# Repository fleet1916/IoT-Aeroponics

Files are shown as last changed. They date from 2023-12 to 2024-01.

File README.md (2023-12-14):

# IoT-Aeroponics
Authors: Zheyuan Zheng (zz534@cornell.edu), Kyle Harris (kah289@cornell.edu), Department of Mechanical and Aerospace Engineering, Cornell University. 
Under the support of Prof. Perrine Pepiot, MAE and Prof. Magdalena Maria Julkowska, Boyce Thompson Institute. 

An basic IoT solution for aeroponics system control based on Arduino 
This project uses a ESP 8266 to set up WiFi and server to allow the control of multiple aeroponics systems to raise multiple plants. 
It includes 4 basic types of the station: The Main Control Terminal (MCT), The Bucket Control Station (BCS), Data Collection and Calibration Station (DCS), and In Bucket Stand (IBS). 
A set of system would include 1 MCT, maximum of ( 8 BCS + 40 IBS ) and 1 DCS. 
The Main Control Terminal sends out input command through a WiFi server. All the bucket control station connects and receives the signal from the server to determine the bucket number, mode and control perimeter.

The Bucket Control Station controls 5 bucket. It can operate the 5 buckets'mist makers separately in time control mode, percentage control mode and on/off mode. It also provide power for the fans that distribute the mist evenly in the buckets as well.                     
Time control mode turns on the mistmaker for X seconds and turn off the mistmaker for Y seconds. X and Y can be input through the MCT. 
Percentage mode set the mist level to a certain IR sensor reading by turning on and off the mist maker . 
This reading is determined by a steady state mist level IR sensor reading multiplied by the percentage input throught he MCT. 
For the on/off mode, the MCT can control the mist maker on/off directly 

The Data Collection and Calibration Station have no control authority over mist maker and the fan. It is a interface to record the mist level in the bucket during normal operation and determine the steady state IR sensor reading for calibration purposes, which is necessary for the Percentage mode to work properly. Sensor value A is obtained by reading the sensor value without turning on the mist maker.  Another sensor value B can be obtained by set the bucket control mode to on/off and turn on the mist maker for more than 20 mins. The calibration reading is the absolute value of the difference between A and B. After getting the calibration reading, change the fullmist value to the calibration value for the control mode to operate in its best condition. 

The In Bucket Stand is a stand to host fan and sensor for the controlling and mist distribution purposes. It needs to be connected to the BCS. 

Look for the bill of materials and assembly insturction to make the system and installing libraries in you computer. 
Upload the code in each folder to the corresponding arduino/ESP8266 board to set up the functions of the system

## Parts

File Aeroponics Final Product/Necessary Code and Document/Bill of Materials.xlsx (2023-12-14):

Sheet: Main Control Terminal
Name | Quantity | Amazon ASIN | Amazon name | Note
Arduino MEGA 2560 controller | 1 | N/A
PCB | 1 | B0BK76L5BD | SchmalzTech Double Sided ENIG Protoboard, Solderable Breadboard, Electronic Circuit Board for DIY Prototype Circuit, FR4, Plated Through Hole Solder Prototype Board, ST-Proto (1" x 2")
Dupont wires | 17 |  |  | Assorted dupont female- male, male-male jumper wires
Female Dupont Connector | 6
Short jumper wires | 4
ESP8266 WiFi Module | 1 | B010N1ROQS | HiLetgo 3pcs ESP8266 ESP-01 Serial WiFi Wireless Transceiver Wireless Module Development Board LWIP AP+STA Compatible with Arduino
Keypad | 1 | B086ZGKDK9 | DIYmalls 4x4 Matrix Membrane Keypad 16 Key Keyboard Module Array Switch for Arduino ESP32
LCD screen | 1 | B0C6SGK21R | DIYmalls 20x4 IIC I2C 2004 LCD Display Screen Module 5V White Character Blue Backlight with Serial Adapter Board PCF8574 for Arduino (Pack of 2)
Header Pin | 14
Remote Control Casing | 1 |  |  | CAD in Github

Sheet: Bucket Control Station
Name | Quantity | Amazon ASIN | Amazon name | Note
Arduino Nano | 1 | ‎B0713XK923 | ELEGOO Nano Board CH 340/ATmega+328P Without USB Cable, Compatible with Arduino Nano V3.0 (Nano x 3 Without Cable)
PCB | 2 | B0BK76L5BD | SchmalzTech Double Sided ENIG Protoboard, Solderable Breadboard, Electronic Circuit Board for DIY Prototype Circuit, FR4, Plated Through Hole Solder Prototype Board, ST-Proto (1" x 2")
Relay | 5 | B07BVXT1ZK | ARCELI 5PCS 5V One Channel Relay Module Board Shield 5v Relay Module for PIC AVR DSP ARM for Relay | Note that in Amazon introduction, it sasy the coil voltage is 12V. But the actual coil voltage is 5 V, which is correct for our application
WiFi Module | 1 | B010N1ROQS | HiLetgo 3pcs ESP8266 ESP-01 Serial WiFi Wireless Transceiver Wireless Module Development Board LWIP AP+STA Compatible with Arduino
Switch | 6 | B07XC5KB8D | TWTADE 10Pcs Rocker Switch ON/Off SPST 2Pin Latching Toggle Switch Snap Round with Pre-Wired 6A/250V 10A/125V AC for Boat,Car etc.KCD1-X-Y
Power Distribution Panel | 1 | B093PWRJS9 | WayinTop PCB Double-Layer Wiring Power Distribution Board Kit, 2 x 12 Position Power Distribution Module 2 Inputs 2 x 13 Outputs for DC AC 24V 10A
Voltage Converter | 1 | B076P4C42B | Wolfwhoop PW-D Control Buck Converter 6-24V to 5V 1.5A Step-Down Regulator Module Power Inverter Volt Stabilizer
LED | 6 | N/A |  | Any 5V LED would work
heat shrink tube | 1 | N/A
Female Dupont Connector | 6 | N/A
Female Round 2.1mm*5.5 mm | 6 | B071VTBQNG | MILAPEAK (Real 18AWG 43x2pcs Wires) 20pcs Female DC Power Pigtail Cable, 12V 5A DC Connectors for CCTV Security Camera and Lighting Power Adapter (2.1mm x 5.5mm, Ultra Thick)
Jumper Wires |  | N/A
JST-XH connector | 10 | B07YKHV46N | 5 Pairs JST-XH 2.54mm 1S 2 Pin Balance Plug Lead Socket Male and Female Connector with 10cm Silicone Wire Cables for Woodland Just Plug Lights 3D Printer
Power Source |  | B08Z7X9F1V | 24 Volt 6 Amp Power Supply Adapter,100-240V AC to DC 24V 6A Power Adapter with 5.5mm x 2.1mm DC Output Jack Transformers US Plug for LED Strip Light,Security Cameras,Printer
Switch Box | 1 |  |  | CAD in Github

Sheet: Data Collection and Calibration
Name | Quantity | Amazon ASIN | Amazon name | Note
PCB | 1 | B0BK76L5BD | SchmalzTech Double Sided ENIG Protoboard, Solderable Breadboard, Electronic Circuit Board for DIY Prototype Circuit, FR4, Plated Through Hole Solder Prototype Board, ST-Proto (1" x 2")
Arduino Nano | 1 | ‎B0713XK923 | ELEGOO Nano Board CH 340/ATmega+328P Without USB Cable, Compatible with Arduino Nano V3.0 (Nano x 3 Without Cable)
LCD | 1 | B071Y6JX3H | SunFounder LCD1602 Module with 3.3V Backlight Compatible with Arduino R3 Mega2560 Raspberry Pi 16x2 Character White on Blue Background
Jumper Wire
Potentiometer for Arduino | 1
JST-XH connector | 10 | B07YKHV46N | 5 Pairs JST-XH 2.54mm 1S 2 Pin Balance Plug Lead Socket Male and Female Connector with 10cm Silicone Wire Cables for Woodland Just Plug Lights 3D Printer

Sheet: In Barrel Stand
Name | Quantity (per Bucket) | Amazon ASIN | Amazon name | Note
24V Fan | 1 | B00N1Y3T9G | GDSTIME 80mm x 80mm x 25mm 24V Brushless DC Cooling Fan
Infrared Sensor | 1
Mist Maker | 1 | B00P91ZFPA | AGPTEK Aluminum Mini Mist Maker Fogger Water Fountain Pond Fog Machine Atomizer, Perfect for Halloween, Christmas and Other Holidays
Fan and Sensor stand | 1 |  |  | CAD in Github

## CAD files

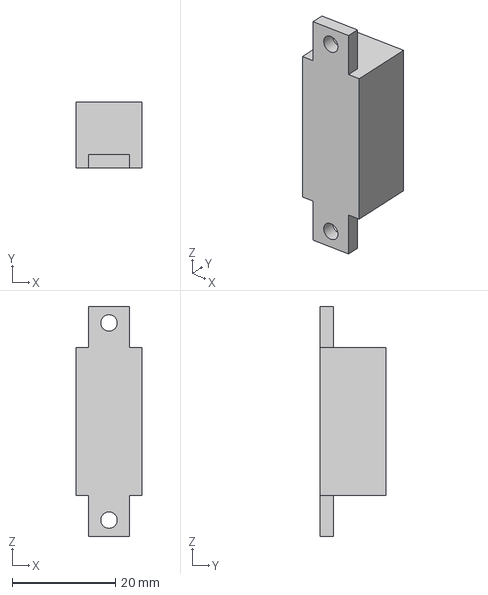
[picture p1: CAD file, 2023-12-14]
Aeroponics Final Product/CAD Files/Electronic Models/Infrared Sensor.step
12.7 x 12.7 x 44.4 mm

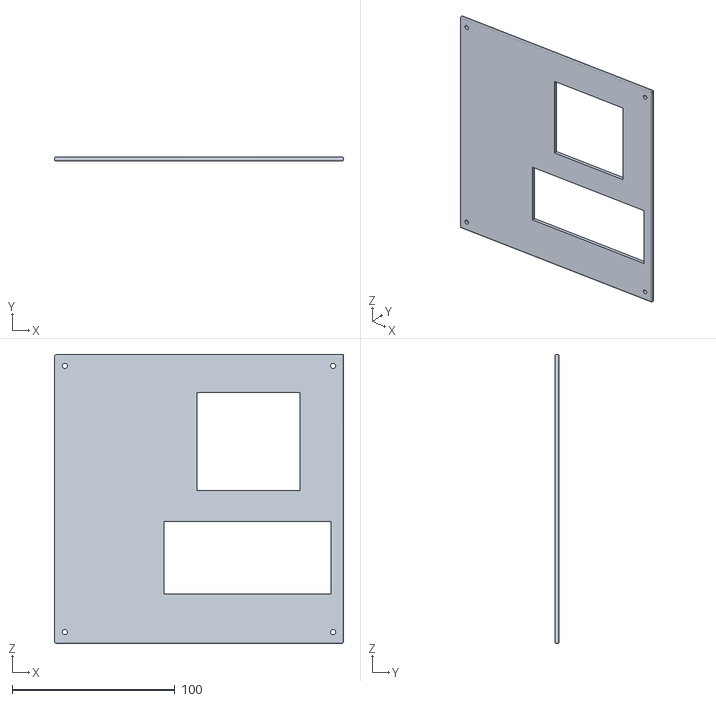
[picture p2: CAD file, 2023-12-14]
Aeroponics Final Product/CAD Files/Remote Control Lid.stl
177.8 x 2.54 x 177.8

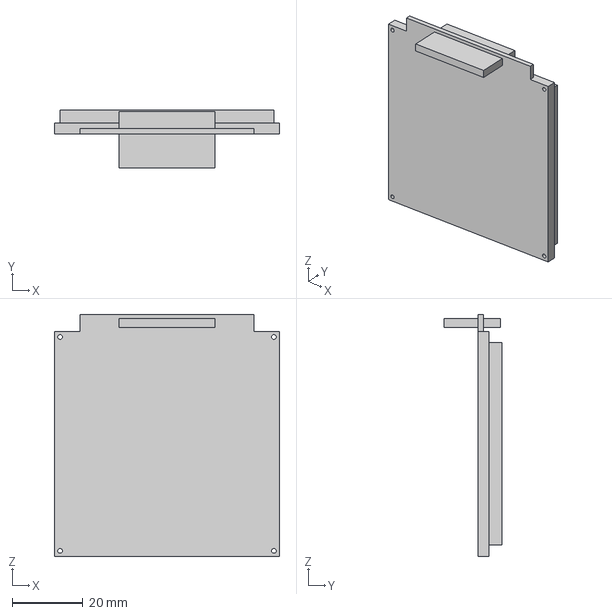
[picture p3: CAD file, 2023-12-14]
Aeroponics Final Product/CAD Files/Electronic Models/Keypad.step
63.5 x 16.3 x 68.3 mm

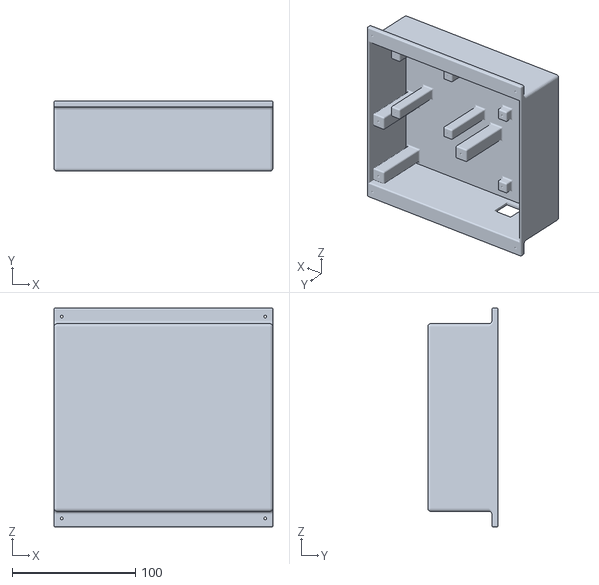
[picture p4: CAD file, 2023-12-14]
Aeroponics Final Product/CAD Files/Remote Control Hull.stl
177.8 x 57.2 x 177.8

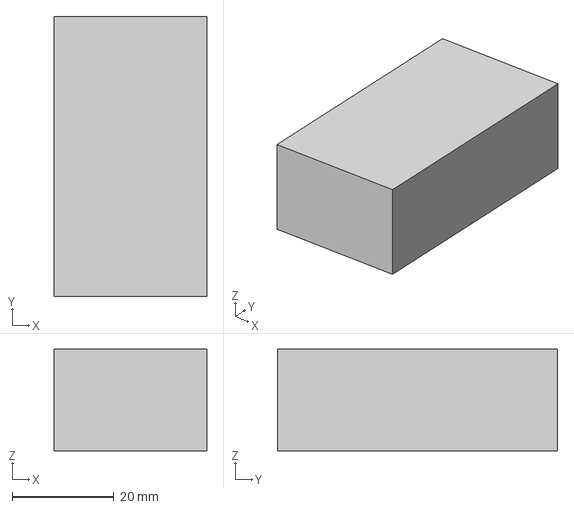
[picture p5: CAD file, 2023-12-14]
Aeroponics Final Product/CAD Files/Electronic Models/Battery.step
30.0 x 55.0 x 20.0 mm

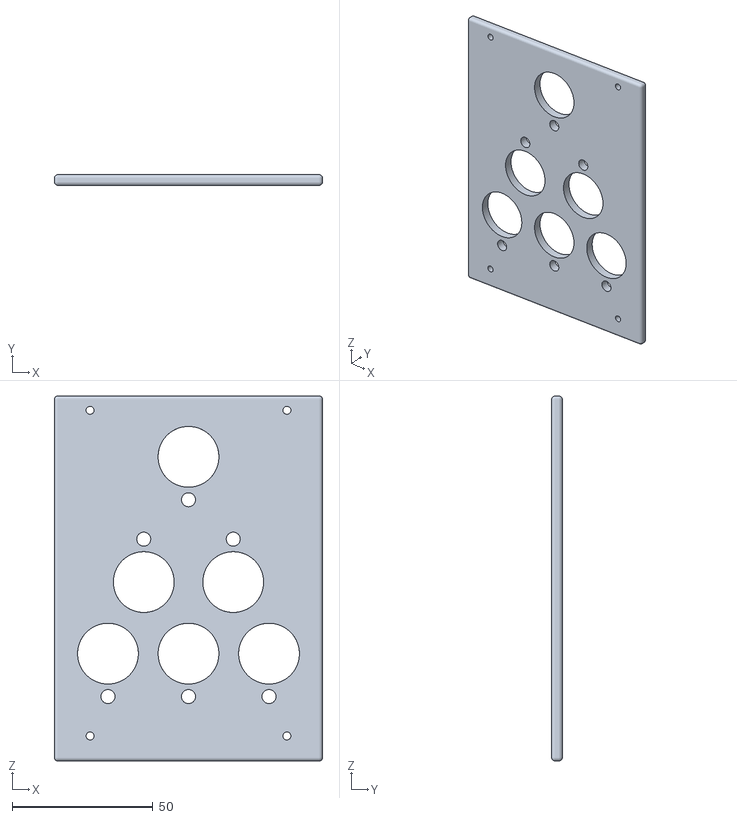
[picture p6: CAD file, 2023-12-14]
Aeroponics Final Product/CAD Files/Switch Box Lid.stl
95.2 x 3.81 x 129.5

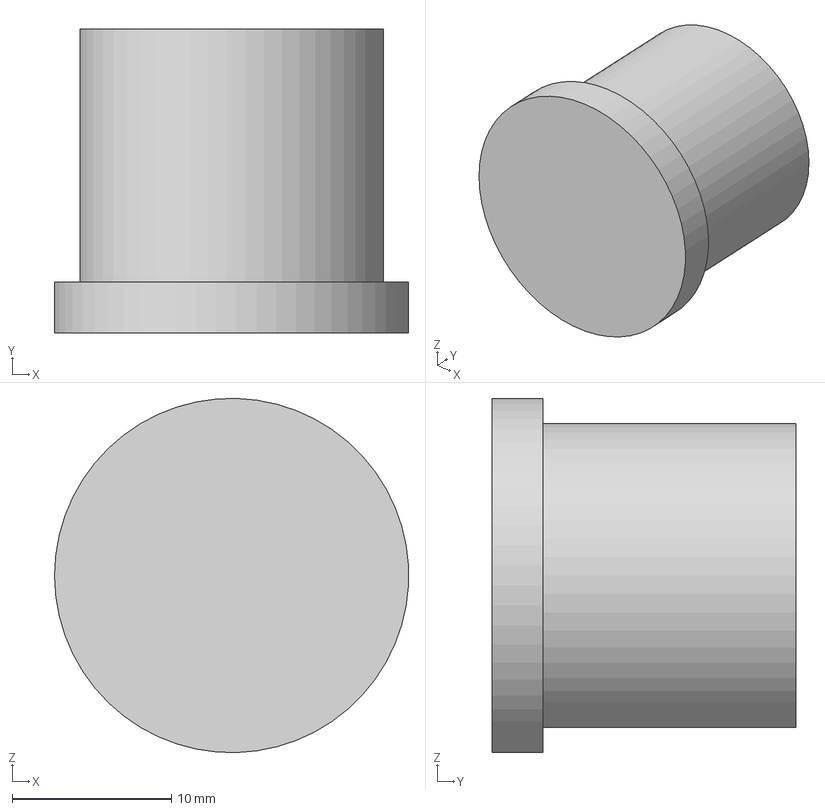
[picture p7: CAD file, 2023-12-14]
Aeroponics Final Product/CAD Files/Electronic Models/Switch.step
22.2 x 19.0 x 22.2 mm

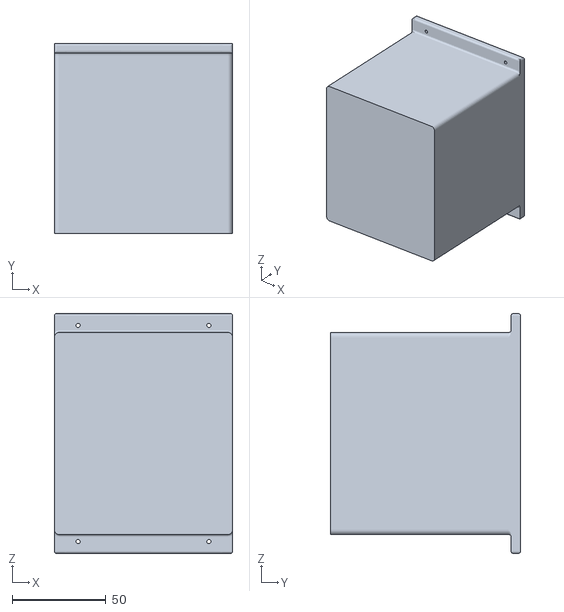
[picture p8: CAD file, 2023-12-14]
Aeroponics Final Product/CAD Files/Switch Box Hull.stl
95.2 x 101.6 x 128.3

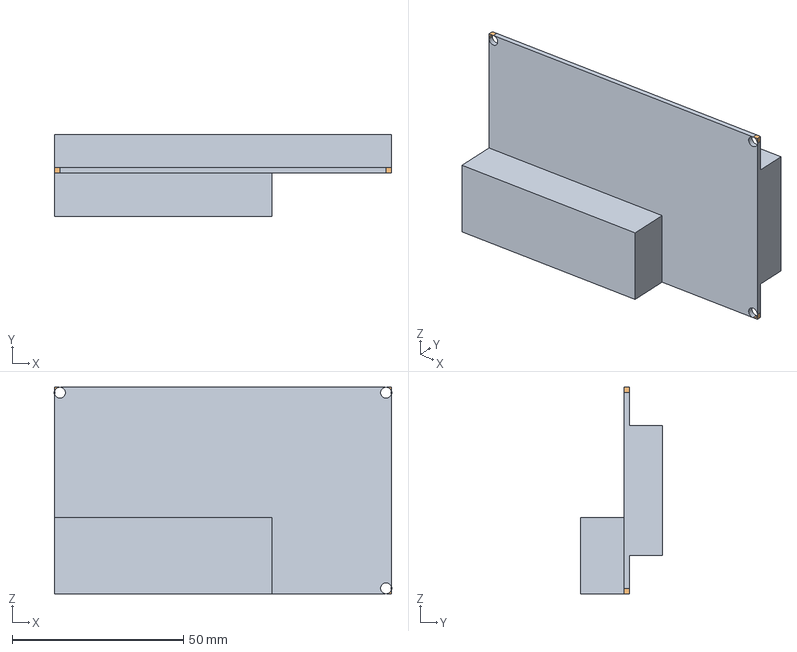
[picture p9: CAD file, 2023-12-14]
Aeroponics Final Product/CAD Files/Electronic Models/LCD.step
98.4 x 23.8 x 60.3 mm

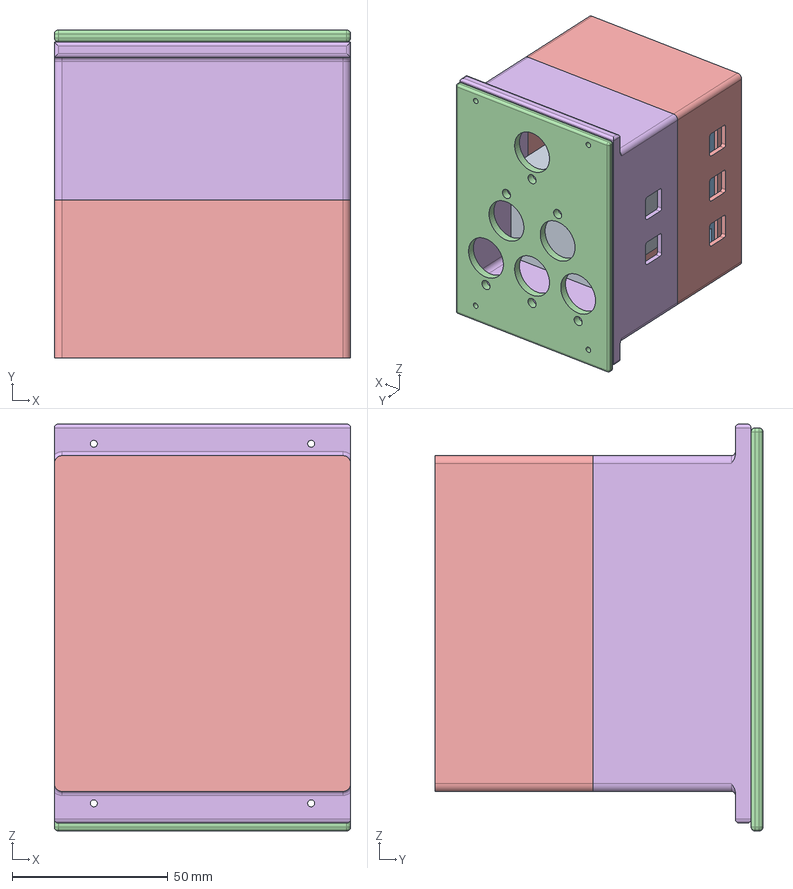
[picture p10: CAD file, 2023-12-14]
Aeroponics Final Product/CAD Files/Switch Box.step
95.2 x 105.4 x 130.8 mm
Power Supply Board
LED Board
Switch Board

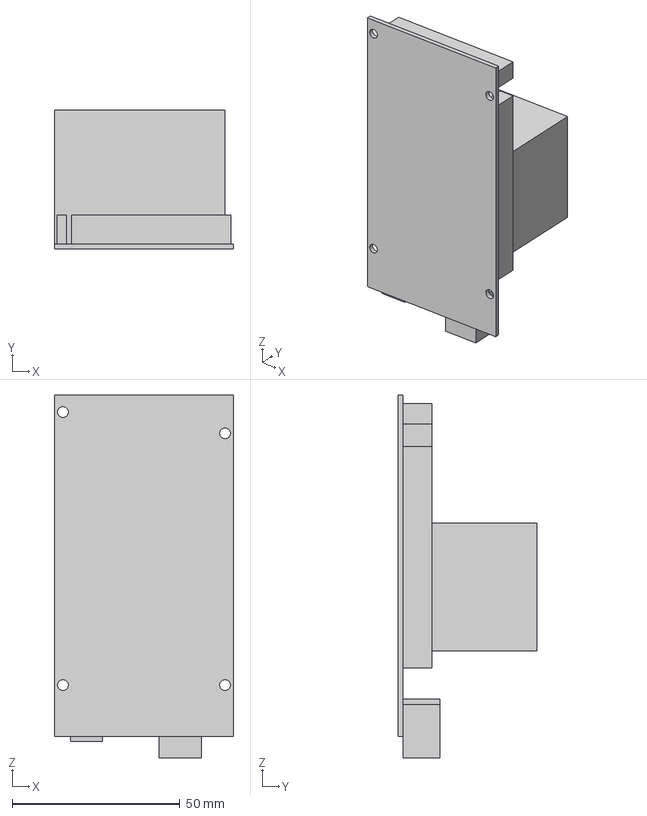
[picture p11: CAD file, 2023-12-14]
Aeroponics Final Product/CAD Files/Electronic Models/Arduino.step
53.3 x 41.5 x 108.1 mm

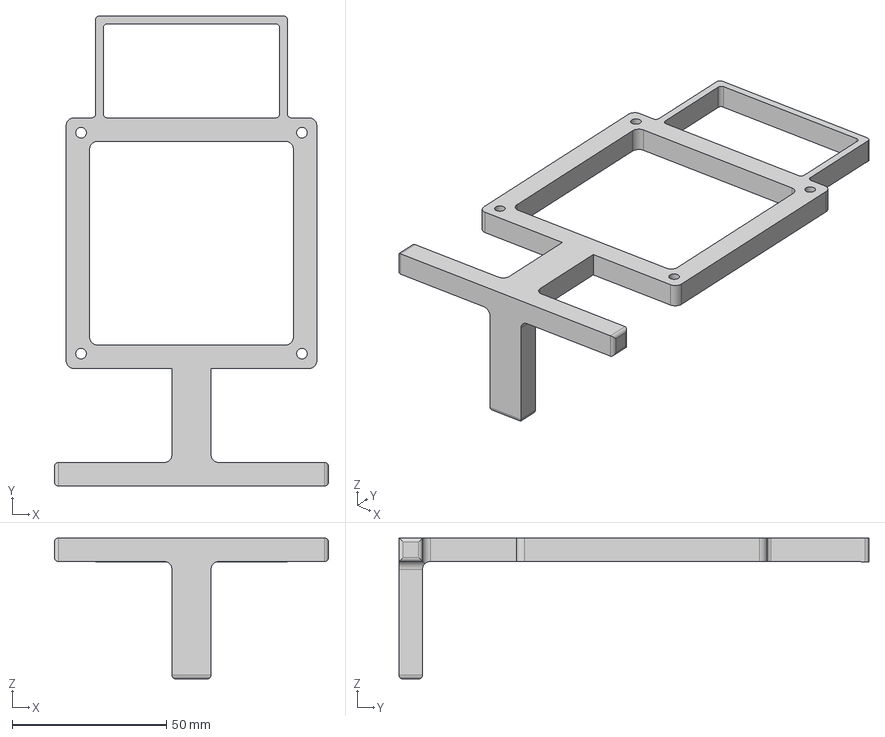
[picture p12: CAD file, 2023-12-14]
Aeroponics Final Product/CAD Files/Fan and Sensor Holder.step
88.9 x 152.4 x 45.7 mm

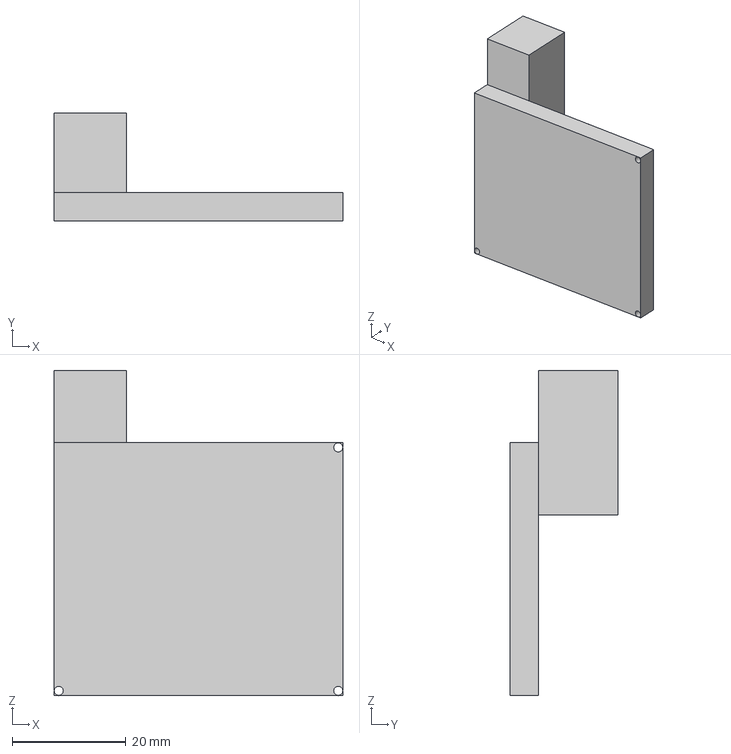
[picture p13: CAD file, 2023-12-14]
Aeroponics Final Product/CAD Files/Electronic Models/LED Board.step
50.8 x 19.0 x 57.1 mm

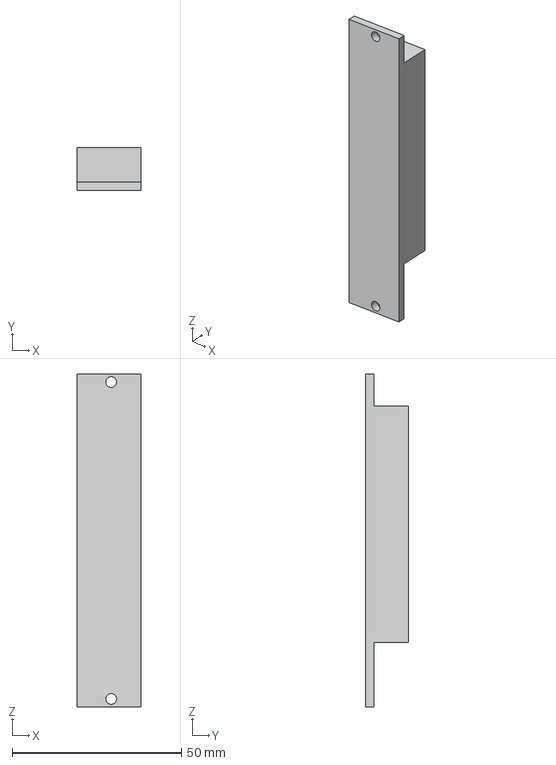
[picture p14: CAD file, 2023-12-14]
Aeroponics Final Product/CAD Files/Electronic Models/Relay.step
19.0 x 12.7 x 98.4 mm

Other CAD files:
Aeroponics Final Product/CAD Files/Electronic Models/Power Supply Board.step
Aeroponics Final Product/CAD Files/Fan and Sensor Holder.stl

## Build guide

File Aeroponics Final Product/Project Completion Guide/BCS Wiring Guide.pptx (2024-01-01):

## BCS Wiring Guide

## Fixing the wire on the Power

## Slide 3

Switch

5.5 mm Connector

To 24V Power Source

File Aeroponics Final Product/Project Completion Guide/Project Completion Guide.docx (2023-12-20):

Project Completion Guide

Zheyuan Zheng zz534@cornell.edu

The project completion guide covers things that need to be done for the first prototype to function properly. You can go to the Rapid Prototyping Lab or the Maker Lab for 3D printing.

MCT:

3D print the casing and install the components in the casing. The CAD files of the casing is in the CAD files folder. The name of the files are “Remote Control Hull” and “Remote Control Lid”.

Note that the Keypad is plugged into the Arduino Mega at the moment. After securing the keypad on the casing, you will need female-male Dupont connector wires to connect it to the Arduino. From left to right, the keypad pins are connected to 36,38,40,42,44,46,48,50,52, GND.

BCS:

Examine the current CAD files of the BCS casing and adjust them according to the need of the current electronics. The files are “Switch Box Hull” and “Switch Hull Lid”. 3D print them after adjustment.

Connect wiring for the fan and mist maker. See the Wiring Guide for the Wiring.

See the BCS Assembly Guide to make new ones.

DCS:

Design a casing for the DCS. It will also work without the casing.

IBS:

Install the fan and the sensor. Solder and connect the sensor with the Dupont Connector.

Further Improving the system:

Set up 2 way WiFi communication to replace the DCS.

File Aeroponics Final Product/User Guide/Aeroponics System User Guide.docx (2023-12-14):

Aeroponics User Guide

12/12/2023 Zheyuan Zheng zz534@cornell.edu

Abbreviations:

The Main Control Terminal | MCT
The Bucket Control Station | BCS
Data Collection and Calibration Station | DCS
In Bucket Stand | IBS

Connector Type

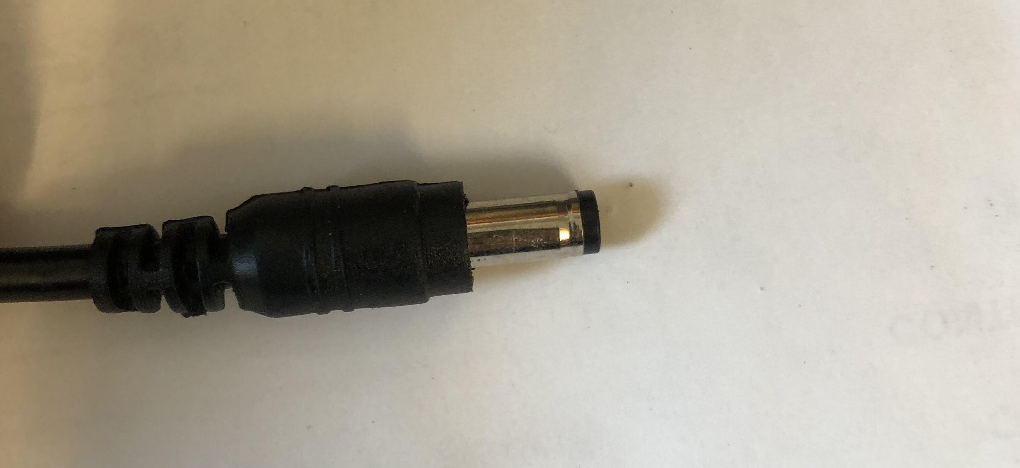
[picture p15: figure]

5.5 mm Round Connector

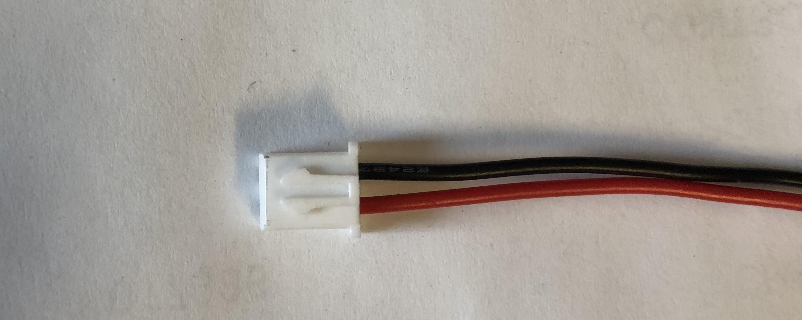
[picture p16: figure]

JST-XH Connector

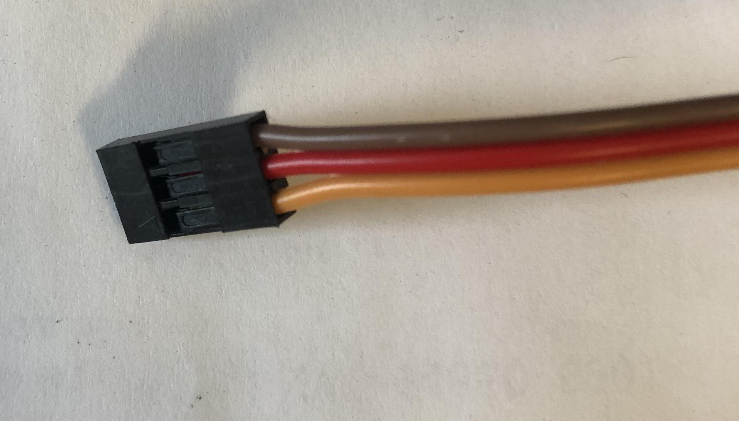
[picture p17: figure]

Dupont Connector

Assembly Instruction before Connecting to Power

Normal Operations:

For normal operation, the BCS can operate 5 buckets.

Plug the connector of the mist maker for each bucket to the connection holes on the BCS.
Plug the JST-XH connector on the IBS to the corresponding BCS connector. This connector is for the fan.
Plug the Dupont Connector to the corresponding connector on the BCS as well. The Dupont connector is for the sensor.

Using DCS for calibration and sensing:

Connect the fan and the mist maker as in normal mode. The DCS will act as the as the intermediate between the BCS and IBS.

Plug the connector of the mist maker for each bucket to the connection holes on the BCS.
Plug the JST-XH connector on the IBS to the corresponding BCS connector. This connector is for the fan.
Connect the IBS Dupont connectors to the ones on the DCS
connect the DCS connectors to the corresponding BCS connectors.
Connect the DCS to your computer with the micro USB wire
Turn the knob around until you see text on the screen.
You should see “Initializing “ with a series of jumping numbers. In the end the screen will show “calib value K”
K is your base value. Now turn on the mist maker with the BCS in on/off mode (See normal operation guide). Wait for about 20 mins for the mist in the bucket to reach
Read the reading displayed by the LCD screen “M”
The calibration value “C” is the absolute value of the difference between M and K.
Remove the DCS from the connection between the BCS and the IBS. Disconnect DCS from your computer.

Turning on the System and Sending Command through the MCT

Plug the 9V DC power source to the 5.5 mm round connector on the MCT. IMPORTANT NOTE: Distinguish the 9V DC power and 24V DC power! They both use 5.5 mm round connector. DO NOT connect 24V power to the MCT!
The MCT LCD screen should be lit. Wait for about 30 seconds for the welcome screen to appear.
Connect the 24V DC power to the BCS through the 5.5 mm round connector to it.
Turn on the main manual switch on the BCS. The Calibration LED should lit up for a few seconds, which indicates normal operation of the BCS.
Turn on the manual fan switches on the BCS.
You can always press “D” to erase any input shown in the input section.
Set the station number: Set the station number by press “A” followed by the station number desired. Press “#” to set the station number in the command section.
Set the mode: Press “B” followed by the mode you desire. Mode 1 is the Time Control Mode, Mode 2 is the Percentage Mode, and Mode 3 is the on/off mode. Press “#” sign to set the mode in the command section
Mode Specific Parameter: Time Control Mode The time parameter follows the format “cXXcYY” where XX is two digits on time and YY is two digits off time. For example, a 2 minutes on time and 3 minutes off time sequence is written as “c02c03”. Press the “#” sign to input the parameter in the command section.
Mode Specific Parameter: Percentage Mode The percentage parameter follows the format “cXXX” where XXX is a three digits parameter ranging from 0-100. Note that as the percentage goes below 20%-30%, the mist level in the bucket will be unstable due to sensor inaccuracies. Press the “#” sign to input the parameter in the command section.
Mode Specific Parameter: On/Off Mode Press “c” then “#” to switch between on and off
After inputting the command section, press “*” to send the command.
The LED on the BCS will indicate if the mist maker is on. Note that the LED will only be on if the mist maker is on.

To achieve the best data accuracy, calibrate the BCS before using percentage mode.

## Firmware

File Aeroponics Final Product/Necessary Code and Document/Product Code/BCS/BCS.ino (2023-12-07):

#include <PID_v1.h>

int wifi=1;

double fullmist=130;
int satlimit=300000;
unsigned long starttime = 0;
unsigned long smplintvl = 1000;
unsigned long snsrintvl = 5000; 
unsigned long pM1 = 0; 
unsigned long pM2 = 0;
char j;

int mistPina=2;
int ledPina=3;
int mistPinb=4;
int ledPinb=5;
int mistPinc=6;
int ledPinc=7;
int mistPind=8;
int ledPind=9;
int mistPine=10;
int ledPine=11;

int calibpin=12;
int pwrpin=13;

const int ira = A1;
const int irb = A2;
const int irc = A3;
const int ird = A4;
const int ire = A5;

int mistStatea;
int mistStateb;
int mistStatec;
int mistStated;
int mistStatee;

double sVa[10];
double cVa[10];
double rslta;
double avgsnsra;
unsigned long pMa3 = 0;
unsigned long pMa4 = 0; 
unsigned long intvla[2];
double mistlevelprcnta=0;
double ontimea;
double setvaluea=mistlevelprcnta*fullmist/100;
int modea = 2;

//Bucket b numbers
double sVb[10];
double cVb[10];
double rsltb;
double avgsnsrb;
unsigned long pMb3 = 0;
unsigned long pMb4 = 0; 
unsigned long intvlb[2];
double mistlevelprcntb=0;
double ontimeb;
double setvalueb=mistlevelprcntb*fullmist/100;
int modeb = 2;

double sVc[10];
double cVc[10];
double rsltc;
double avgsnsrc;
unsigned long pMc3 = 0;
unsigned long pMc4 = 0; 
unsigned long intvlc[2];
double mistlevelprcntc=0;
double ontimec;
double setvaluec=mistlevelprcntc*fullmist/100;
int modec = 2;

double sVd[10];
double cVd[10];
double rsltd;
double avgsnsrd;
unsigned long pMd3 = 0;
unsigned long pMd4 = 0; 
unsigned long intvld[2];
double mistlevelprcntd=0;
double ontimed;
double setvalued=mistlevelprcntd*fullmist/100;
int moded = 2;

double sVe[10];
double cVe[10];
double rslte;
double avgsnsre;
unsigned long pMe3 = 0;
unsigned long pMe4 = 0; 
unsigned long intvle[2];
double mistlevelprcnte=0;
double ontimee;
double setvaluee=mistlevelprcnte*fullmist/100;
int modee = 2;



 
unsigned long time=0;
PID PIDa(&avgsnsra, &ontimea, &setvaluea, 100, 8, 100, DIRECT);
PID PIDb(&avgsnsrb, &ontimeb, &setvalueb, 100, 8, 100, DIRECT);
PID PIDc(&avgsnsrb, &ontimeb, &setvalueb, 100, 8, 100, DIRECT);
PID PIDd(&avgsnsrb, &ontimeb, &setvalueb, 100, 8, 100, DIRECT);
PID PIDe(&avgsnsrb, &ontimeb, &setvalueb, 100, 8, 100, DIRECT);



String strtotal;
String buck;
String mode;
String pct; 
String ont;
String offt;
String id; 
int buc =6;
int mod = 2;
int pc;
int idk;
unsigned long on;
unsigned long off;


char dataStr[100] = "";
char buffer[7];


void setup() {
  Serial.begin(115200);
  //pinMode set up 
    pinMode(mistPina, OUTPUT);
    pinMode(ledPina, OUTPUT);
    pinMode(mistPinb, OUTPUT);
    pinMode(ledPinb, OUTPUT);
    pinMode(mistPinc, OUTPUT);
    pinMode(ledPinc, OUTPUT);
    pinMode(mistPind, OUTPUT);
    pinMode(ledPind, OUTPUT);
    pinMode(mistPine, OUTPUT);
    pinMode(ledPine, OUTPUT);
    pinMode(pwrpin,OUTPUT);
    pinMode(calibpin,OUTPUT);
    digitalWrite(pwrpin,HIGH);
    digitalWrite(calibpin,HIGH);



  //calibration
  for (j = 0; j < 10; j++) {
    cVa[j] =analogRead(ira) ;
    cVb[j] =analogRead(irb) ;
    cVa[j] =analogRead(irc) ;
    cVb[j] =analogRead(ird) ;
    cVa[j] =analogRead(ire) ;
    delay(50);
  }
  rslta = 0;
  rsltb = 0;
  rsltc = 0;
  rsltd = 0;
  rslte = 0;
  for (j = 0; j < 10; j++) {
    rslta = rslta + cVa[j]; 
    rsltb = rsltb+ cVb[j];
    rsltc = rsltc + cVc[j]; 
    rsltd = rsltd+ cVd[j];
    rslte = rslte + cVe[j]; 
  }
  rslta = rslta / 10+55; 
  rsltb = rsltb / 10+40; 
  rsltc = rsltc / 10; 
  rsltd = rsltd / 10; 
  rslte = rslte / 10; 
  delay(1000);
  starttime = millis();

  pM1 = starttime; 
  pM2 = starttime;
  Serial.print("calib value:");
  Serial.println(rslta);


  PIDa.SetOutputLimits(500, satlimit);
  PIDa.SetMode(AUTOMATIC);
  PIDb.SetOutputLimits(500, satlimit);
  PIDb.SetMode(AUTOMATIC);
  PIDc.SetOutputLimits(500, satlimit);
  PIDc.SetMode(AUTOMATIC);
  PIDd.SetOutputLimits(500, satlimit);
  PIDd.SetMode(AUTOMATIC);
  PIDe.SetOutputLimits(500, satlimit);
  PIDe.SetMode(AUTOMATIC);
  digitalWrite(calibpin,LOW);
}

void loop() {
  dataStr[0] = 0;
  command();
  sense();
  time=millis();
  if (buc==0) {
    if (mod==0) {
      modea=0;
    } else if (mod == 1){
      modea=1;
    } else if (mod == 2) {
      modea=2;
    } else if (mod == 3) {
      modea=3;
    }

    mistlevelprcnta=pc;
    intvla [0]=on*1000;
    intvla [1]=off*1000;
  } else if (buc==1) {
    if (mod==0) {
      modeb=0;
    } else if (mod == 1) {
      modeb=1;
    } else if (mod == 2) {
      modeb=2;

    } else if (mod == 3) {
      modeb=3;
    } else if (mod == 4) {
      modeb=4;
    }
    mistlevelprcntb=pc;
    intvlb [0]=on*1000;
    intvlb [1]=off*1000;
  } else if (buc==2) {
    if (mod==0) {
      modec=0;
    } else if (mod == 1) {
      modec=1;
    } else if (mod == 2) {
      modec=2;
    } else if (mod == 3) {
      modec=3;
    } else if (mod == 4) {
      modec=4;
    }
    mistlevelprcntc=pc;
    intvlc [0]=on*1000;
    intvlc [1]=off*1000;
  } else if (buc==3) {
    if (mod==0) {
      moded=0;
    } else if (mod == 1) {
      moded=1;
    } else if (mod == 2) {
      moded=2;

    } else if (mod == 3) {
      moded=3;
    } else if (mod == 4) {
      moded=4;
    }
    mistlevelprcntd=pc;
    intvld [0]=on*1000;
    intvld [1]=off*1000;
  } else if (buc==4) {
    if (mod==0) {
      modee=0;
    } else if (mod == 1) {
      modee=1;
    } else if (mod == 2) {
      modee=2;

    } else if (mod == 3) {
      modee=3;
    } else if (mod == 4) {
      modee=4;
    }
    mistlevelprcnte=pc;
    intvle [0]=on*1000;
    intvle [1]=off*1000;
  }

  if (modea==1) {
    controlmodea();
  } else if (modea==0) {
    timemodea();
  } else if (modea==2) {
    digitalWrite(mistPina,LOW);
    digitalWrite(ledPina,LOW);
  } else if (modea==3) {
    digitalWrite(mistPina,HIGH);
    digitalWrite(ledPina,HIGH);
  }
  if (modeb== 1) {
    controlmodeb();
  } else if (modeb ==0 ) {
    timemodeb();
  } else if (modeb ==2) {
    digitalWrite(mistPinb,LOW);
    digitalWrite(ledPinb,LOW);
  } else if (modeb==3) {
    digitalWrite(mistPinb,HIGH);
    digitalWrite(ledPinb,HIGH);
  }
  if (modec==1) {
    controlmodec();
  } else if (modec==0) {
    timemodec();
  } else if (modec==2) {
    digitalWrite(mistPinc,LOW);
    digitalWrite(ledPinc,LOW);
  } else if (modec==3) {
    digitalWrite(mistPinc,HIGH);
    digitalWrite(ledPinc,HIGH);
  }

  if (moded== 1) {
    controlmoded();
  } else if (moded ==0 ) {
    timemoded();
  } else if (moded==2) {
    digitalWrite(mistPind,LOW);
    digitalWrite(ledPind,LOW);
  } else if (moded==3) {
    digitalWrite(mistPind,HIGH);
    digitalWrite(ledPind,HIGH);
  }
   if (modee==1) {
    controlmodee();
  } else if (modee==0) {
    timemodee();
  } else if (modee==2) {
    digitalWrite(mistPine,LOW);
    digitalWrite(ledPine,LOW);
  } else if (modee==3) {
    digitalWrite(mistPine,HIGH);
    digitalWrite(ledPine,HIGH);
  }




}

void command () {
    while (Serial.available() > 0 ) {
    strtotal  = Serial.readString();    
    id=strtotal.substring(14);
    idk=id.toInt();
    if (idk == wifi) {
    buck=strtotal.substring(0);
    mode=strtotal.substring(2);
    pct=strtotal.substring(4,7);
    ont=strtotal.substring(8,10);
    offt=strtotal.substring(11,13);
    buc=buck.toInt();
    mod=mode.toInt();
    pc=pct.toInt();
    Serial.println(idk);
    Serial.println(buc);
    Serial.println(mod);
    Serial.println(pc);
    on =(unsigned long) ont.toInt();
    off = (unsigned long) offt.toInt();
    Serial.println(on);
    Serial.println(off);
    if ((on == 0 || off == 0 )&& mod==0) {
      mod=2;
    }
    if (pct == 0 && mod == 1) {
      mod=2;
    }
    }
   }

}

void controlmodea () {
    setvaluea=mistlevelprcnta*fullmist/100;
    PIDa.Compute();
    pMa3 = time;
    if (time - pMa3 < ontimea) {
        mistStatea=HIGH;
    } else {
        mistStatea=LOW;
    }
    digitalWrite(mistPina, mistStatea);
    digitalWrite(ledPina,mistStatea);
   
    
}

void controlmodeb () {
    setvalueb=mistlevelprcntb*fullmist/100;
    PIDb.Compute();
    pMb3 = time;
    if (time - pMb3 < ontimeb) {
        mistStateb=HIGH;
    } else {
        mistStateb=LOW;
    }
    digitalWrite(mistPinb, mistStateb);
    digitalWrite(ledPinb,mistStateb);
    if (time - pM2 >= snsrintvl) {
    pM2 = time;
    }

}

void controlmodec () {
    setvaluec=mistlevelprcntc*fullmist/100;
    PIDc.Compute();
    pMc3 = time;
    if (time - pMc3 < ontimec) {
        mistStatec=HIGH;
    } else {
        mistStatec=LOW;
    }
    digitalWrite(mistPinc, mistStatec);
    digitalWrite(ledPinc,mistStatec);
   
    
}

void controlmoded () {
    setvalued=mistlevelprcntd*fullmist/100;
    PIDd.Compute();
    pMd3 = time;
    if (time - pMd3 < ontimed) {
        mistStated=HIGH;
    } else {
        mistStated=LOW;
    }
    digitalWrite(mistPind, mistStated);
    digitalWrite(ledPind,mistStated);
   
    
}

void controlmodee () {
    setvaluee=mistlevelprcnte*fullmist/100;
    PIDe.Compute();
    pMe3 = time;
    if (time - pMe3 < ontimee) {
        mistStatee=HIGH;
    } else {
        mistStatee=LOW;
    }
    digitalWrite(mistPine, mistStatee);
    digitalWrite(ledPine,mistStatee);
   
    
}

void timemodea () {
    digitalWrite(mistPina, mistStatea);
    digitalWrite(ledPina,mistStatea);
    if (time- pMa4 >= intvla[mistStatea]) {
    pMa4 = time;
      if (mistStatea == LOW) {
      mistStatea = HIGH;
      } else {
      mistStatea = LOW;
      }
    }
  }

void timemodeb () {
    digitalWrite(mistPinb, mistStateb);
    digitalWrite(ledPinb,mistStateb);
    if (time- pMb4 >= intvlb[mistStateb]) {
    pMb4 = time;
      if (mistStateb == LOW) {
      mistStateb = HIGH;
      } else {
      mistStateb = LOW;
      }
    }
  }

void timemodec () {
    digitalWrite(mistPinc, mistStatec);
    digitalWrite(ledPinc,mistStatec);
    if (time- pMc4 >= intvlc[mistStatec]) {
    pMc4 = time;
      if (mistStatec == LOW) {
      mistStatec = HIGH;
      } else {
      mistStatec = LOW;
      }
    }
  }

void timemoded () {
    digitalWrite(mistPind, mistStated);
    digitalWrite(ledPind,mistStated);
    if (time- pMd4 >= intvld[mistStated]) {
    pMd4 = time;
      if (mistStated == LOW) {
      mistStated = HIGH;
      } else {
      mistStated = LOW;
      }
    }
  }

void timemodee () {
    digitalWrite(mistPine, mistStatee);
    digitalWrite(ledPine,mistStatee);
    if (time- pMe4 >= intvle[mistStatee]) {
    pMe4 = time;
      if (mistStatee == LOW) {
      mistStatee = HIGH;
      } else {
      mistStatee = LOW;
      }
    }
  }

void sense () {
  if (time - pM1 >= smplintvl) {
        pM1 = time;
        for (j = 0; j < 10; j++) {
            sVa[j] =analogRead(ira)-rslta;
            sVb[j] =analogRead(irb)-rsltb;
            sVc[j] =analogRead(irc)-rsltc;
            sVd[j] =analogRead(ird)-rsltd;
            sVe[j] =analogRead(ire)-rslte;
        }
    }
    avgsnsra=0;
    avgsnsrb=0;
    avgsnsrc=0;
    avgsnsrd=0;
    avgsnsre=0;
    for (j = 0; j < 10; j++) {
    avgsnsra = avgsnsra + sVa[j]; 
    avgsnsrb = avgsnsrb + sVb[j]; 
    avgsnsrc = avgsnsrc + sVc[j]; 
    avgsnsrd = avgsnsrd + sVd[j];
    avgsnsre = avgsnsre + sVe[j]; 
    }
    avgsnsra = avgsnsra / 10; 
    avgsnsrb = avgsnsrb / 10; 
    avgsnsrc = avgsnsrc / 10; 
    avgsnsrd = avgsnsrd / 10; 
    avgsnsre = avgsnsre / 10; 

  if (time - pM2 >= snsrintvl) {
    pM2 = time;


    dtostrf(avgsnsra, 5, 1, buffer);  //5 is minimum width, 1 is precision; float value is copied onto buff
    strcat( dataStr, buffer); //append the converted float
    strcat( dataStr, ", "); //append the delimiter

    dtostrf(avgsnsrb, 5, 1, buffer);  //5 is minimum width, 1 is precision; float value is copied onto buff
    strcat( dataStr, buffer); //append the converted float
    strcat( dataStr, 0); //terminate correctly 
    //Serial.println(dataStr);
   
  }
}

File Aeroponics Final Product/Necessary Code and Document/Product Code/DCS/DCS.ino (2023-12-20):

#include <LiquidCrystal.h>
const int analogInPin = A1;
double calibValue[10];
double sensorValue[10];
double result;
double avgsensor;
char j;
unsigned long previousMillis2 = 0;
unsigned long starttime = 0;
unsigned long previousMillis1 = 0;      
unsigned long sampleinterval = 1000;
unsigned long sensorinterval = 5000; 
unsigned long time=0;
double mistlevelprcnt=0; //mist level 0-20% will generate inefficient control 
double fullmist=130;
double ontime;
double setvalue=mistlevelprcnt*fullmist/100;
int satlimit=300000;
const int rs = 4, en = 5, d4 = 6, d5 = 7, d6 = 8, d7 = 9;
LiquidCrystal lcd(rs, en, d4, d5, d6, d7);
void setup() {
  Serial.begin(115200);
  lcd.begin(16, 2);
  delay(5000);
  lcd.setCursor(0,0);
  lcd.print("Initializing...");
  delay(5000);
  Serial.println("Calibrating....");
  for (j = 0; j < 20; j++) {
    calibValue[j] =analogRead(analogInPin) ;
    lcd.setCursor(0,1);
    lcd.print(analogRead(analogInPin));
    delay(500);
  }

  result = 0;
  for (j = 10; j <20; j++) {
    result = result + calibValue[j]; // add them up
  }
  result = result / 10; 
  Serial.println("Calibration Value=");
  Serial.println(result);
  lcd.setCursor(0,1);
  lcd.print("calib value");
  lcd.print(result);
  delay(5000);
  Serial.println("Calibration complete!");
  
  lcd.clear();
}

void loop() {
  time = millis();
  sense();
}


void sense () {
  if (time - previousMillis1 >= sampleinterval) {
        previousMillis1 = time;
        for (j = 0; j <= 10; j++) {
            sensorValue[j] =analogRead(analogInPin) ;
        }
    }
    avgsensor=0;
    for (j = 0; j < 10; j++) {
    avgsensor = avgsensor + sensorValue[j]; // add them up
    }
    avgsensor = avgsensor / 10; 

  if (time - previousMillis2 >= sensorinterval) {
    previousMillis2 = time;
    Serial.println(avgsensor);
    lcd.setCursor(1,0);
    lcd.print(avgsensor);
    
  }
}

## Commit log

2023-12-12 Update Bill of Materials.xlsx
    BOM finished
    [Bill of Materials.xlsx]
2023-12-13 BOM+operation manual
    BOM+normal operation manual
    [Bill of Materials.xlsx]
2024-01-01 Create BCS Wiring Guide.pptx
2024-01-02 Update BCS Wiring Guide.pptx
